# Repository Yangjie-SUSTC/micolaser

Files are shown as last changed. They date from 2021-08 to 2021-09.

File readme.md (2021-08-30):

# micolaser-1400

This is the a laserbox design used for microscope. 

There are four lasers: 405, 488,561,640. Excepet 488nm from toptica, all others made by new production laser, China.

Each laser reflected by 0.5 inch mirror and then to 1i inch dichroic mirror to combined into one beam, finally coipled into a single mode fiber by a fiber coupler from thorlabs.

In this depository, you can get all 3D and 2D drawings and part list fort it

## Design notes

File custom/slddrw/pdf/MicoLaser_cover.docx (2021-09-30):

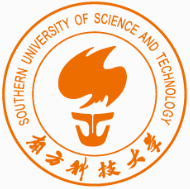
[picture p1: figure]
学校标识- 南方科技大学
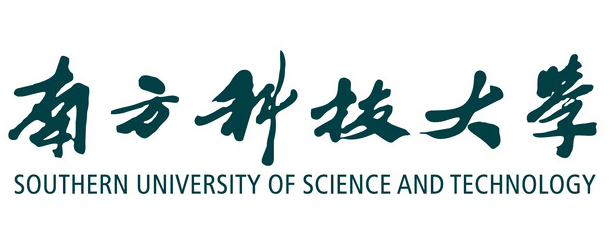
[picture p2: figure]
南方科技大学

MicoLaser-1400 图纸集

杨杰

yangj3@mail.sustech.edu.cn

https://github.com/Yangjie-SUSTC/micolaser

2021/9/30

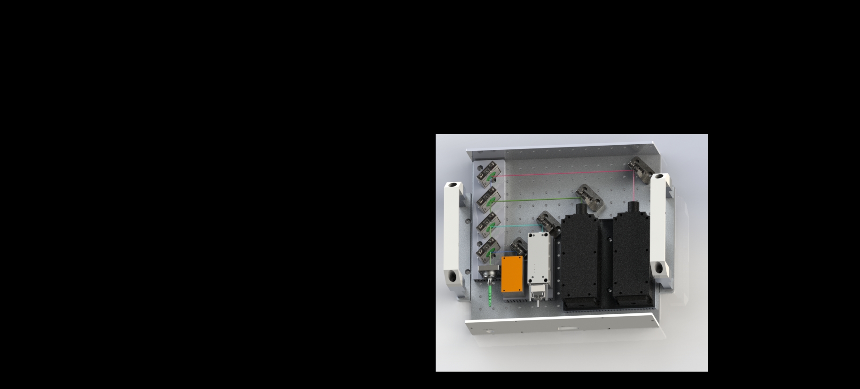
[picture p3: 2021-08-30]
内部渲染.JPG

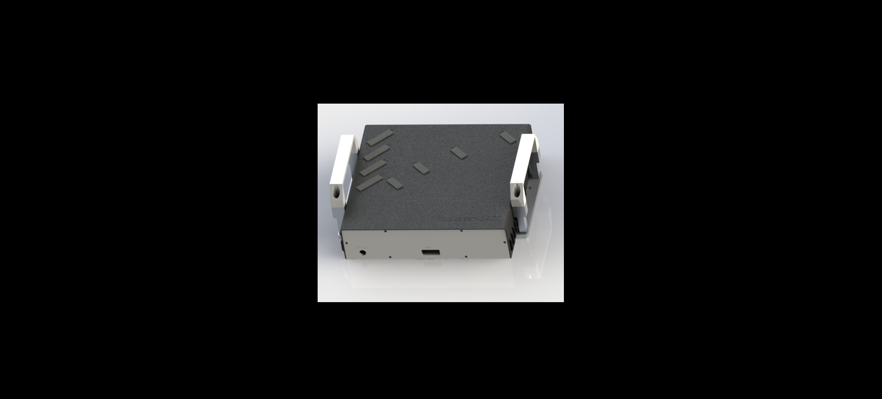
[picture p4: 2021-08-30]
外壳渲染.JPG

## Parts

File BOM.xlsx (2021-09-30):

No. | type | parts | catalog | paramater | manufacture | amount | price | total | link
1 | laser | 405nm | MDL-XS-405 | 200mw | xinchanye | 1 | 14500 | 14500 | http://www.cnilaser.com/PDF/MDL-XS-405.pdf
2 |  | 488nm | Toptica_ibeam_smart | 200mw | Toptica | 1 | 74000 | 74000
3 |  | 561nm | MGL-FN-561 | 300mw | xinchanye | 1 | 37500 | 37500 | http://www.cnilaser.com/PDF/MGL-FN-561.pdf
4 |  | 640nm | MRL-FN-639 | 300mw | xinchanye | 1 | 27000 | 27000 | http://www.cnilaser.com/PDF/MRL-FN-639.pdf
5 | mirror | 1 inch | PF10-03-P01 |  | thorlabs | 1 | 467.29 | 467.29 | PF10-03-P01 平面反射镜，有保护层的银膜，Ø1英寸 (thorlabs.com) (https://www.thorlabs.com/thorproduct.cfm?partnumber=PF10-03-P01)
6 |  | 0.5 inch | PF05-03-P01 |  | thorlabs | 4 | 286.41 | 1145.64 | PF05-03-P01 平面反射镜，有保护层的银膜，Ø1/2英寸 (thorlabs.com) (https://www.thorlabs.com/thorproduct.cfm?partnumber=PF05-03-P01)
7 | dichroic mirror |  | DMLP425 |  | thorlabs | 1 | 1594.96 | 1594.96 | DMLP425 长波通二向色镜，Ø1英寸，起始波长425 nm (thorlabs.com) (https://www.thorlabs.com/thorproduct.cfm?partnumber=DMLP425)
8 |  |  | DMLP505 |  | thorlabs | 1 | 1594.96 | 1594.96 | https://www.thorlabs.com/thorproduct.cfm?partnumber=DMLP505
9 |  |  | DMLP605 |  | thorlabs | 1 | 1594.96 | 1594.96 | https://www.thorlabs.com/thorproduct.cfm?partnumber=DMLP605
10 | fiber output | single mode fiber | P3-405BPM-FC-2 |  | thorlabs | 1 | 1000 | 1000 | https://www.thorlabs.com/thorproduct.cfm?partnumber=P3-405BPM-FC-2
11 |  | fiber coupler | PAF2-A4A |  | thorlabs | 1 | 5460 | 5460 | https://www.thorlabs.com/thorproduct.cfm?partnumber=PAF2-A4A
12 | adjuster |  | hvm-s1r |  | Newport | 1 | 1500 | 1500 | HVM-S1r 反射镜调整架，工业，垂直驱动，1 英寸，2个锁定内六角扳手 (newport.com.cn) (https://www.newport.com.cn/p/HVM-S1r)
13 |  |  | hvm-s1t |  | Newport | 3 | 1600 | 4800 | HVM-S1t 反射镜调整架，工业，垂直驱动，1 英寸，2个锁定内六角扳手 (newport.com.cn) (https://www.newport.com.cn/p/HVM-S1t)
14 |  |  | HVM-05r |  | Newport | 4 | 1360 | 5440 | HVM-05r 反射镜调整架，工业，垂直驱动，后部装载，0.5 英寸， 2个锁定内六角扳手 (newport.com.cn) (https://www.newport.com.cn/p/HVM-05r)
15 |  | Handle | 180mm |  | taobao | 2 | 15 | 30 | 加厚铝合金黑色明装拉手/柜门把手/明装工业设备拉手/工具箱提手-淘宝网 (taobao.com) (https://item.taobao.com/item.htm?id=582286161723&ali_trackid=1_329b5c05201caaaba83558623b89cd20)
16 | magnatic bar | long | 18*60*3 |  | taobao | 4 | 3 | 12 | 宽18*厚2mm K橡胶磁铁条贴 强力软磁条 橡胶磁铁软磁条-淘宝网 (taobao.com) (https://item.taobao.com/item.htm?spm=a230r.1.14.36.3ce538a7w06UFg&id=652351358299&ns=1&abbucket=8)
17 |  | short | 18*40*3 |  | taobao | 4 | 3 | 12
18 | heatsink | 561-640 | 1_561-640nm_heatsink | 6061 Al | custom | 1 | 700 | 700
19 |  |  | 2_405-488nm_heatsink | 6062 Al | custom | 1 | 800 | 800
20 | base |  | 3_DM_base | stainless steel | custom | 1 | 1000 | 1000
21 |  |  | 4_fiberport_stage | stainless steel | custom | 1 | 300 | 300
22 |  |  | 5_0.5mir_base | stainless steel | custom | 1 | 500 | 500
23 |  |  | 6_base | stainless steel | custom | 1 | 2000 | 2000
24 | cover |  | 7_shell | steel | custom | 1 | 2000 | 2000
25 |  |  | 8_back_panel | PMMA | custom | 1 | 200 | 200
26 |  |  | 9_front_panel | PMMA | custom | 1 | 200 | 200
27 |  |  | 10_handle_base | Al | custom | 4 | 100 | 400
28 | pin |  | Φ4*8mm | HPA-2X8-SUS | Misumi | 16 | 6.84 | 109.44 | 圆柱销 A型 m6正公差_价格_多少钱_图片-米思米官网 (misumi.com.cn) (https://www.misumi.com.cn/vona2/detail/221000596791/?pageName=PageCategory)
29 |  |  | Φ2.4*5mm |  |  | 8 | 0.1 | 0.8 | https://item.taobao.com/item.htm?id=530385435625&ns=1&abbucket=15 (https://item.taobao.com/item.htm?spm=a230r.1.14.1.5ab23954NWDenb&id=530385435625&ns=1&abbucket=15)
30 |  |  | Φ1.6*5mm | HPA-1.6X8-SUS |  | 4 | 5.4 | 21.6 | 定位销 圆柱型/A型/m6正公差_价格_多少钱_图片-米思米官网 (misumi.com.cn) (https://www.misumi.com.cn/vona2/detail/221000596791/?pageName=PageCategory)
31 | screw |  | M6*12mm |  | taobao | 17 | 1 | 17
32 |  |  | M4*8mm |  | taobao | 28 | 1 | 28
33 |  |  | M3*6mm |  | taobao | 16 | 0.5 | 8
34 |  |  |  |  |  |  | total | 185936.65

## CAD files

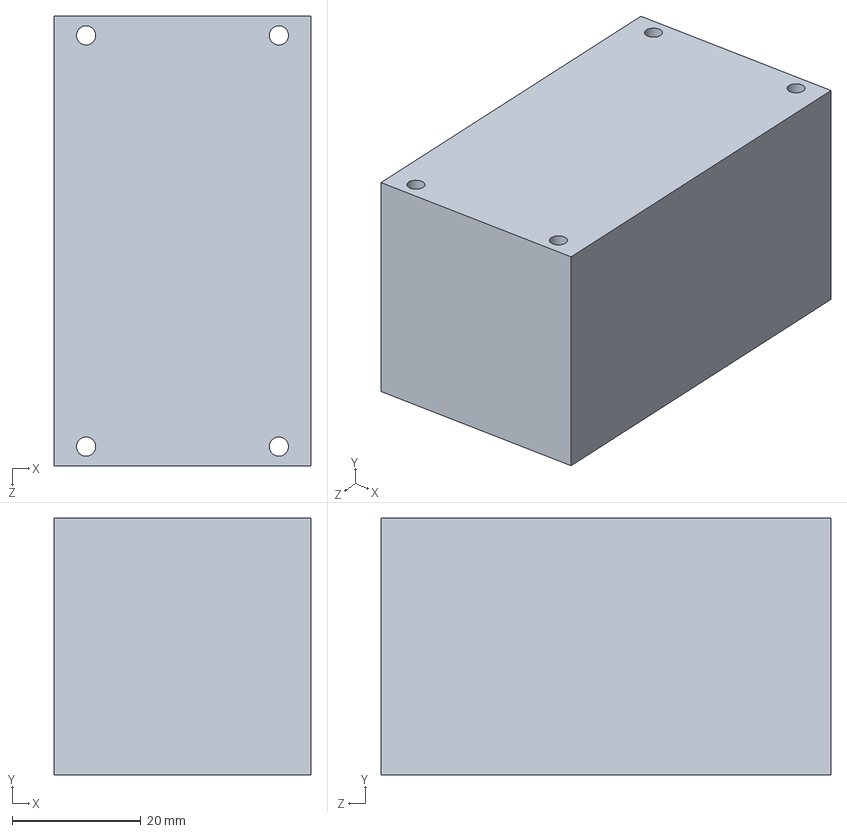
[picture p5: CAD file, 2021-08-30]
commecial/laser/MDL-XS-405.SLDPRT
40.0 x 40.0 x 70.0 mm

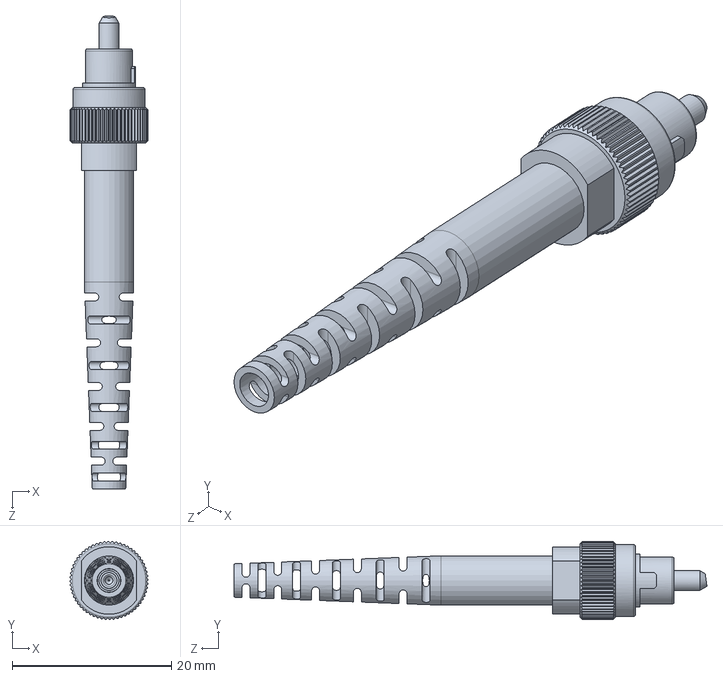
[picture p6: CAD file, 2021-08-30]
commecial/optics/P3-405BPM-FC-2-fiber.sldprt
9.84 x 9.84 x 59.4 mm

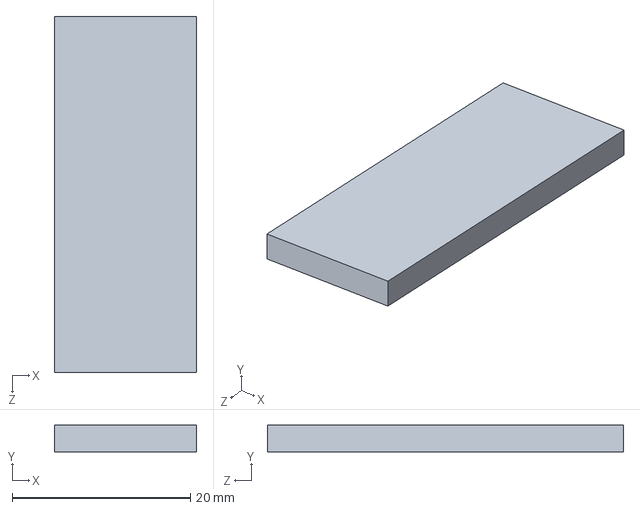
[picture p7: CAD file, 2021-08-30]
commecial/短磁条.SLDPRT
16.0 x 3.00 x 40.0 mm

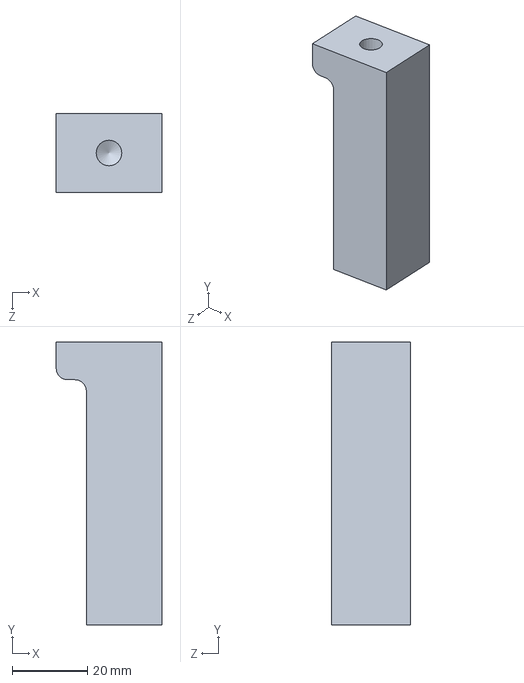
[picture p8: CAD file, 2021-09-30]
custom/10_handle_base.SLDPRT
28.0 x 75.0 x 21.0 mm

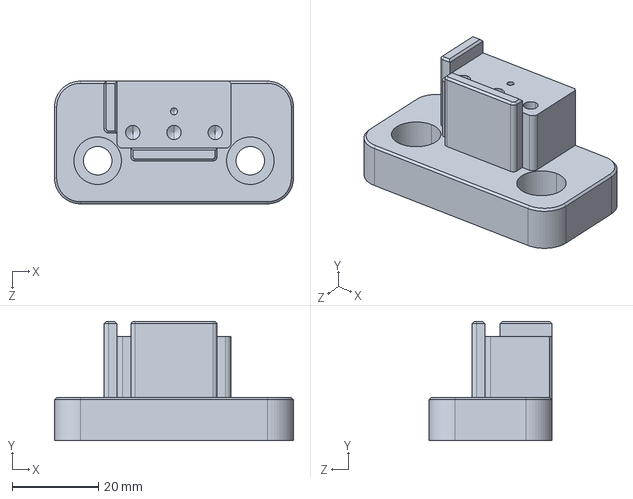
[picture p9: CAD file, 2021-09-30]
custom/micolase1400加工图纸集20210930_南科大/step/5_0.5mir_base.STEP
55.4 x 27.6 x 28.4 mm

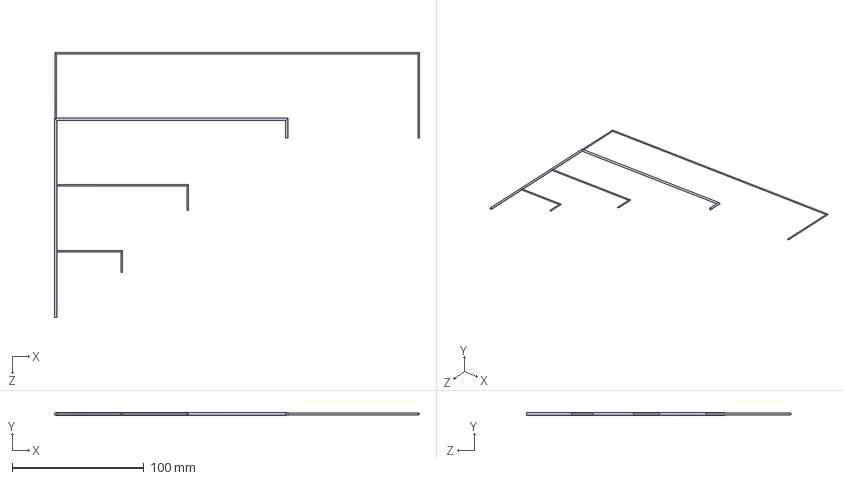
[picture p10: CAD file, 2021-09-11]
optical_path.SLDPRT
276.6 x 2.00 x 200.6 mm

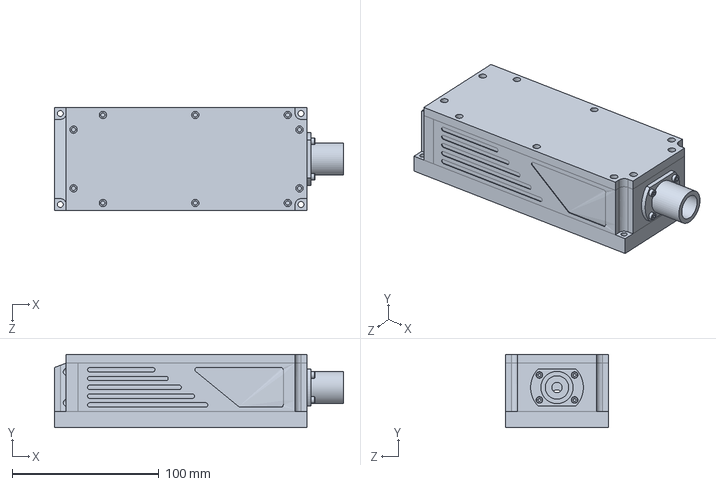
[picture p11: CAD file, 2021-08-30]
commecial/laser/MRL-FN-639.SLDPRT
197.0 x 50.0 x 70.0 mm

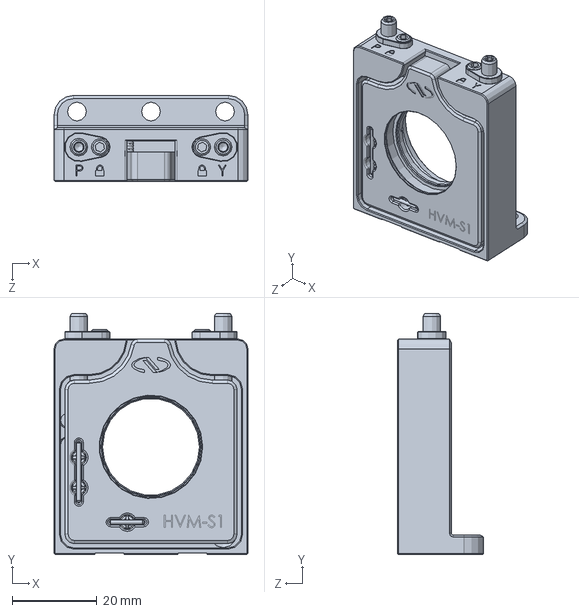
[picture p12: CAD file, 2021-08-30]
commecial/optics/hvm-s1t.SLDPRT
45.7 x 56.8 x 20.3 mm

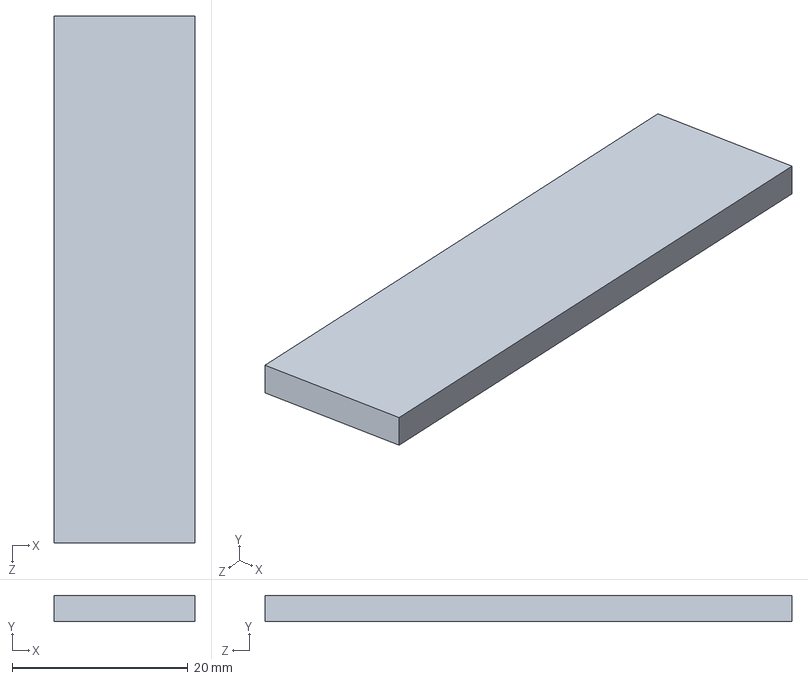
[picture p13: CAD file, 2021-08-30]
commecial/长磁条.SLDPRT
16.0 x 3.00 x 60.0 mm

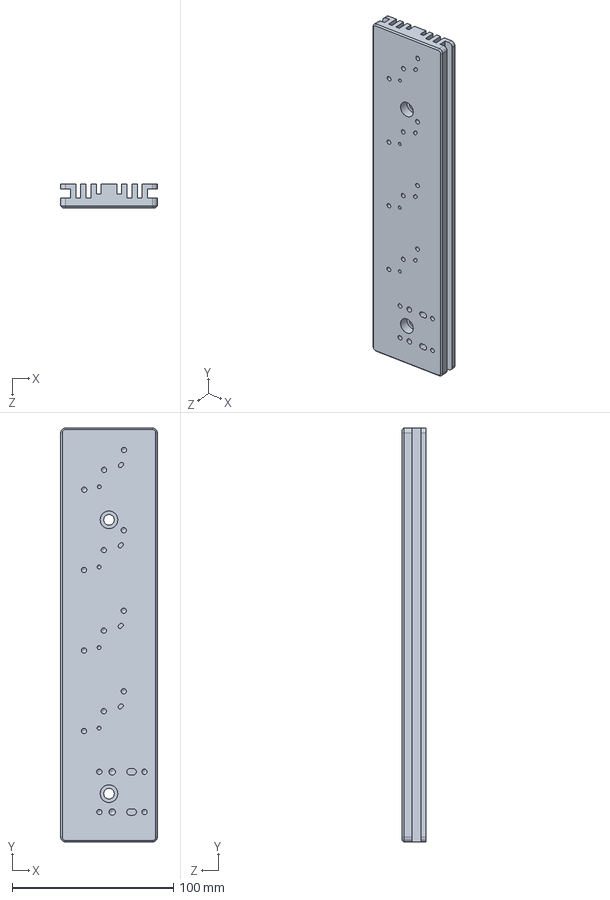
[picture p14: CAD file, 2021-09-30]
custom/3_DM_base.SLDPRT
60.0 x 257.0 x 14.6 mm

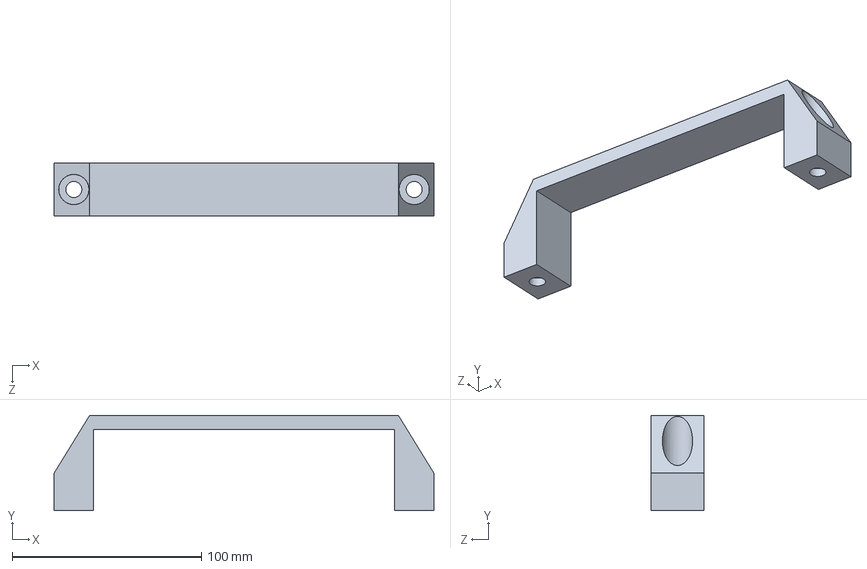
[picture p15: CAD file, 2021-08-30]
commecial/0_Handle.SLDPRT
201.0 x 50.5 x 28.0 mm

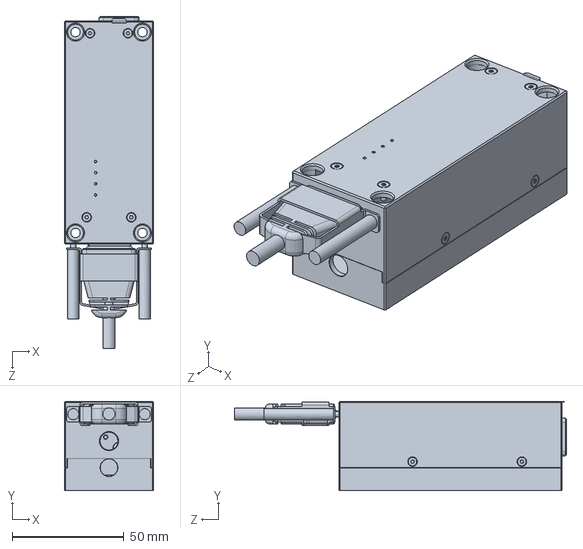
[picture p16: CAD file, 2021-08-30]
commecial/laser/Toptica_ibeam_smart.SLDPRT
40.0 x 40.0 x 148.8 mm

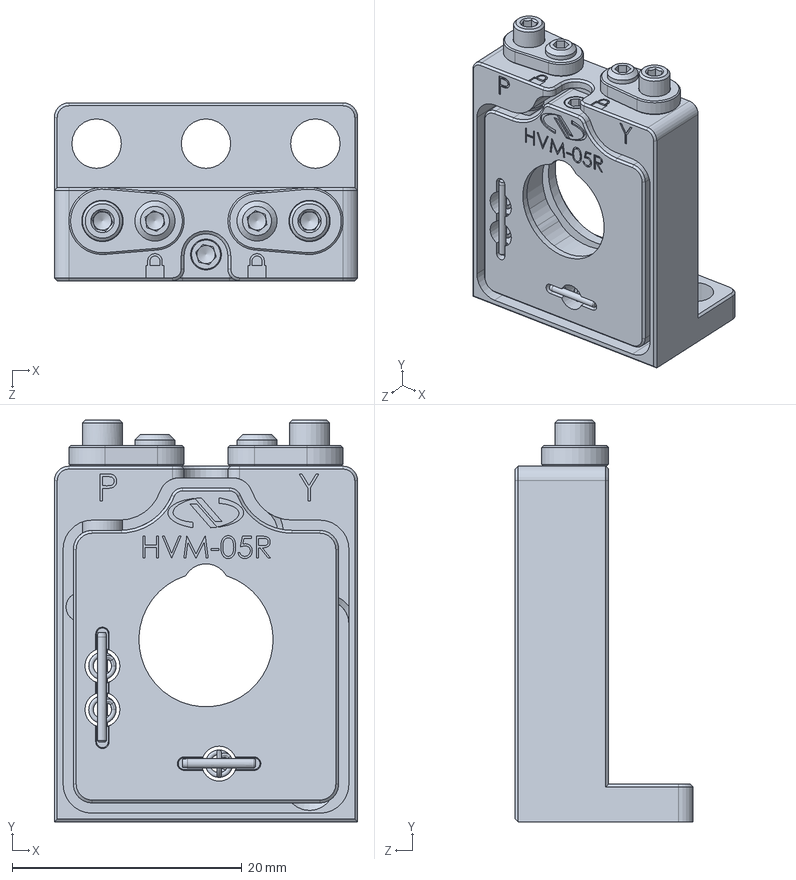
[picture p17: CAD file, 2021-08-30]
commecial/optics/HVM-05r.SLDPRT
26.4 x 35.0 x 15.5 mm

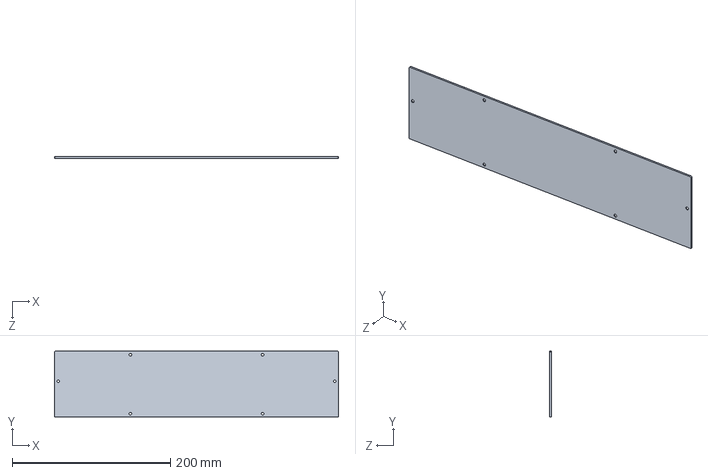
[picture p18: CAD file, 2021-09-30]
custom/8_back_panel.SLDPRT
359.0 x 83.0 x 2.00 mm

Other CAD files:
custom/micolase1400加工图纸集20210930_南科大/dwg/总装.DWG
custom/slddrw/dwg/2_405-488nm_heatsink.DWG
custom/micolase1400加工图纸集20210930_南科大/step/3_DM_base.STEP
custom/slddrw/dwg/1_561-640nm_heatsink.DWG
commecial/optics/hvm-s1r.SLDPRT
commecial/optics/mirror/1inch_Mirror_thorlabs_PF10-03-P01_450nm.SLDPRT
commecial/optics/mirror/DMLP425_thorlabs.sldprt
commecial/optics/mirror/PF05-03-P01-10-thorlabs.sldprt
custom/1_561-640nm_heatsink.SLDPRT
custom/2_405-488nm_heatsink.SLDPRT
custom/4_fiberport_stage.SLDPRT
custom/5_0.5mir_base.SLDPRT
custom/6_base.SLDPRT
custom/7_shell.SLDPRT
custom/9_front_panel.SLDPRT
custom/micolase1400加工图纸集20210930_南科大/dwg/10_handle_base.DWG
custom/micolase1400加工图纸集20210930_南科大/dwg/1_561-640nm_heatsink.DWG
custom/micolase1400加工图纸集20210930_南科大/dwg/2_405-488nm_heatsink.DWG
custom/micolase1400加工图纸集20210930_南科大/dwg/3_DM_base.DWG
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

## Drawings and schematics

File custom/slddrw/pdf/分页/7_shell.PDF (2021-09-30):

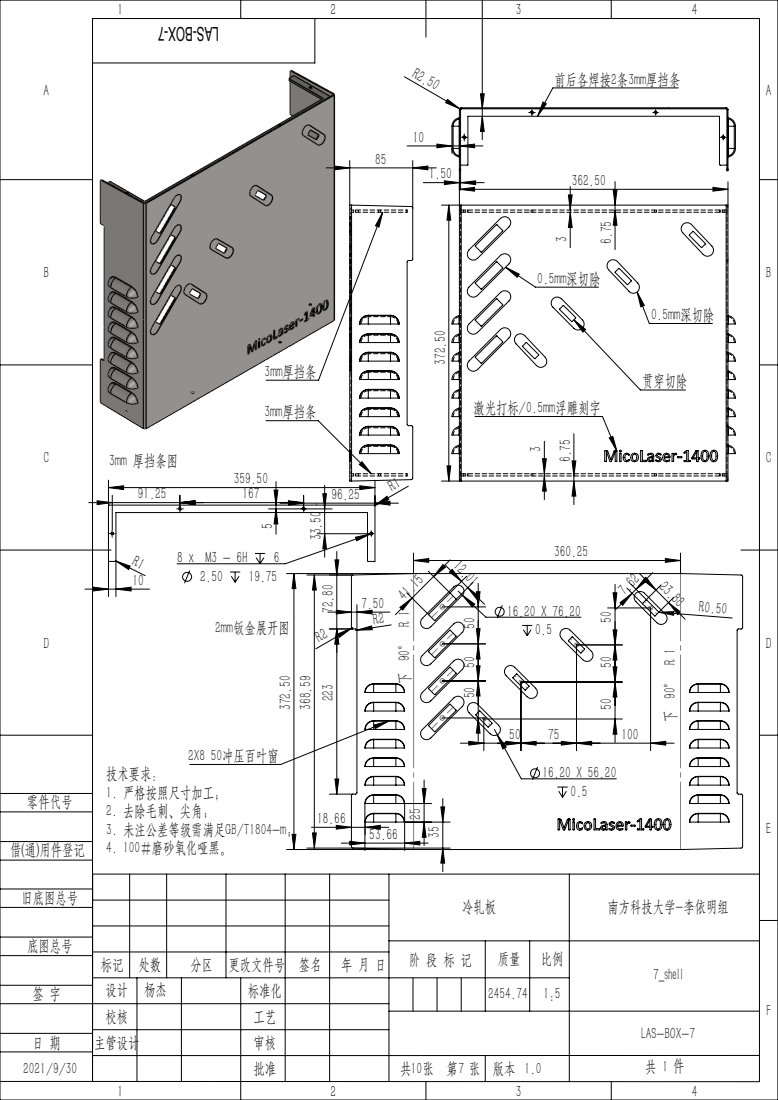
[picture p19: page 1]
2X8 50冲压百叶窗; 3mm 厚挡条图; 1. 严格按照尺寸加工； 2. 去除毛刺、尖角； 3. 未注公差等级需满足GB/T1804-m； 4. 100#磨砂氧化哑黑。

冷轧板 | 南方科技大学-李依明组

阶 段 标 记 | 质量 | 比例 | 7_shell

标记 | 处数 | 分区 | 更改文件号 | 签名 | 年 月 日
设计 | 杨杰 | | 标准化 | | | | | | 2454.74 | 1:5
校核 | | | 工艺
主管设计 | | | 审核

LAS-BOX-7

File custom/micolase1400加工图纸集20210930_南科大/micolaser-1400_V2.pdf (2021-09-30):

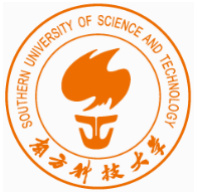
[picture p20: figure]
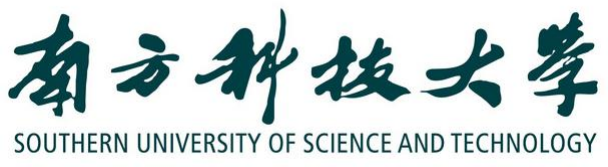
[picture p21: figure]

# MicoLaser-1400 图纸集

杨杰

## yangj3@mail.sustech.edu.cn

## https://github.com/Yangjie-SUSTC/micolaser

2021/9/30

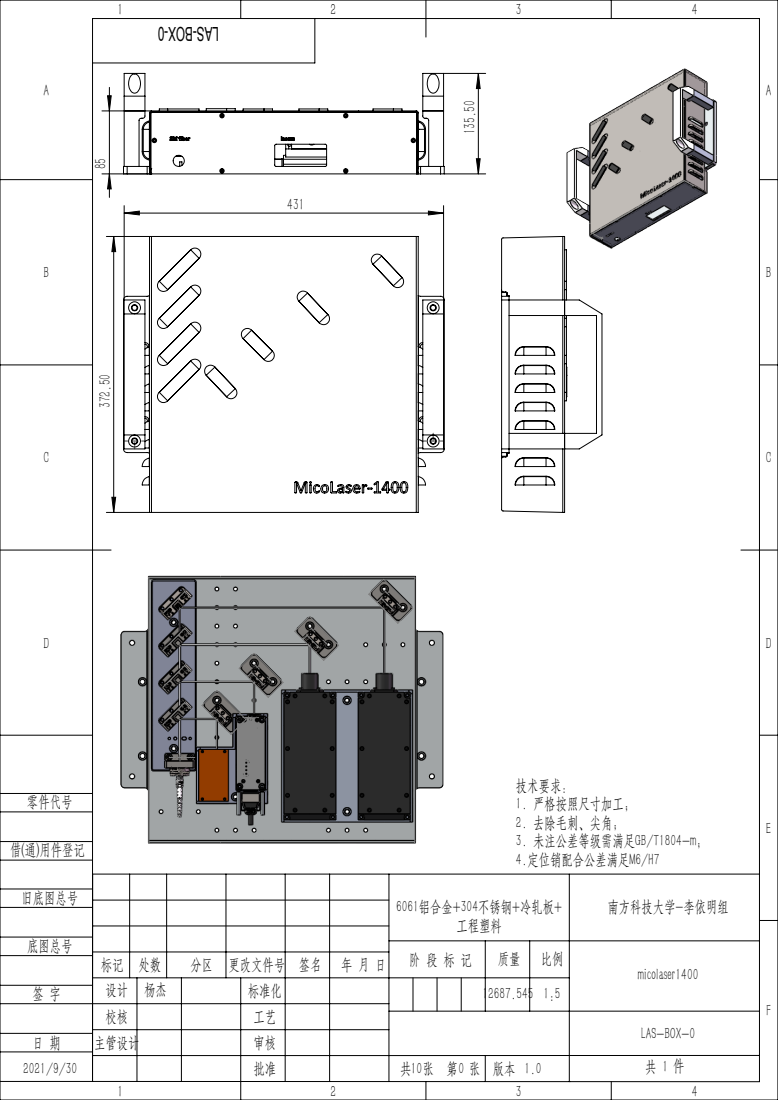
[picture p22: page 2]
底图总号; 旧底图总号; 借(通)用件登记; 零件代号; 技术要求： 1. 严格按照尺寸加工； 2. 去除毛刺、尖角； 3. 未注公差等级需满足GB/T1804-m； 4.定位销配合公差满足M6/H7

6061铝合金+304不锈钢+冷轧板+ 工程塑料 | 南方科技大学-李依明组

阶 段 标 记 | 质量 | 比例 | micolaser1400

标记 | 处数 | 分区 | 更改文件号 | 签名 | 年 月 日
设计 | 杨杰 | | 标准化 | | | | | | 12687.545 | 1:5
校核 | | | 工艺
主管设计 | | | 审核

LAS-BOX-0

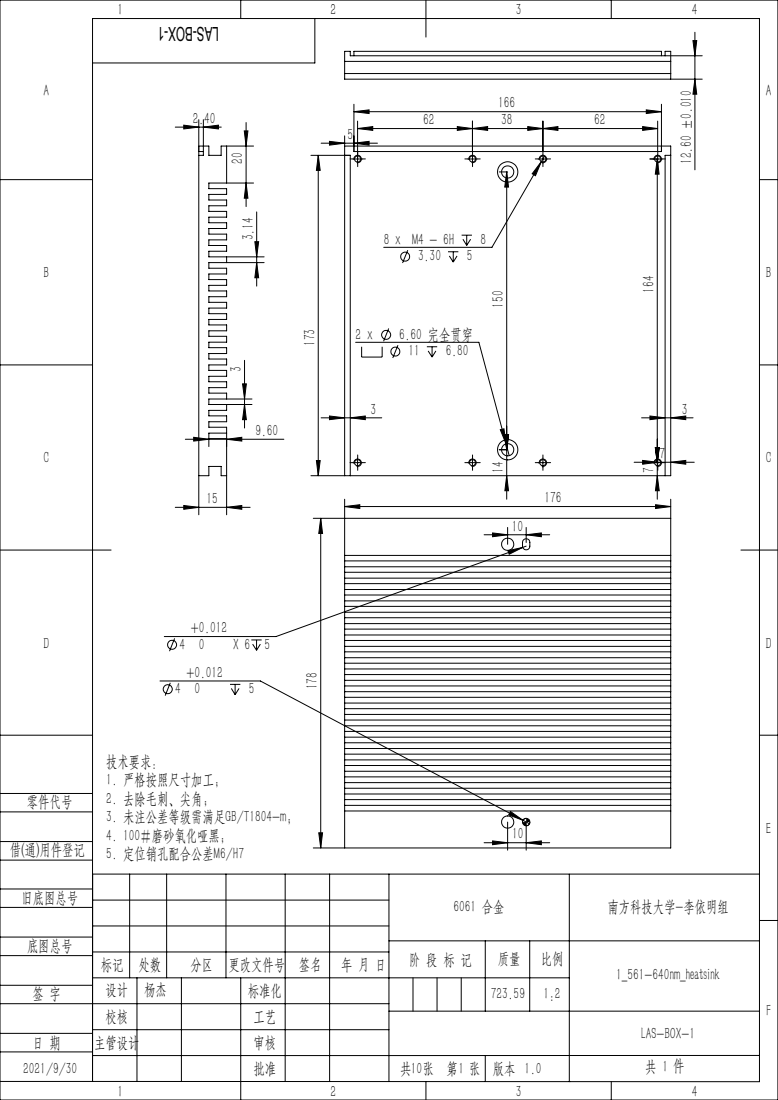
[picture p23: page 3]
6.60 完全贯穿; 底图总号; 旧底图总号; 借(通)用件登记; 零件代号; 技术要求： 1. 严格按照尺寸加工； 2. 去除毛刺、尖角； 3. 未注公差等级需满足GB/T1804-m； 4. 100#磨砂氧化哑黑; 5. 定位销孔配合公差M6/H7

6061 合金 | 南方科技大学-李依明组

阶 段 标 记 | 质量 | 比例 | 1_561-640nm_heatsink

标记 | 处数 | 分区 | 更改文件号 | 签名 | 年 月 日
设计 | 杨杰 | | 标准化 | | | 723.59 | 1:2

24.13 ¹³

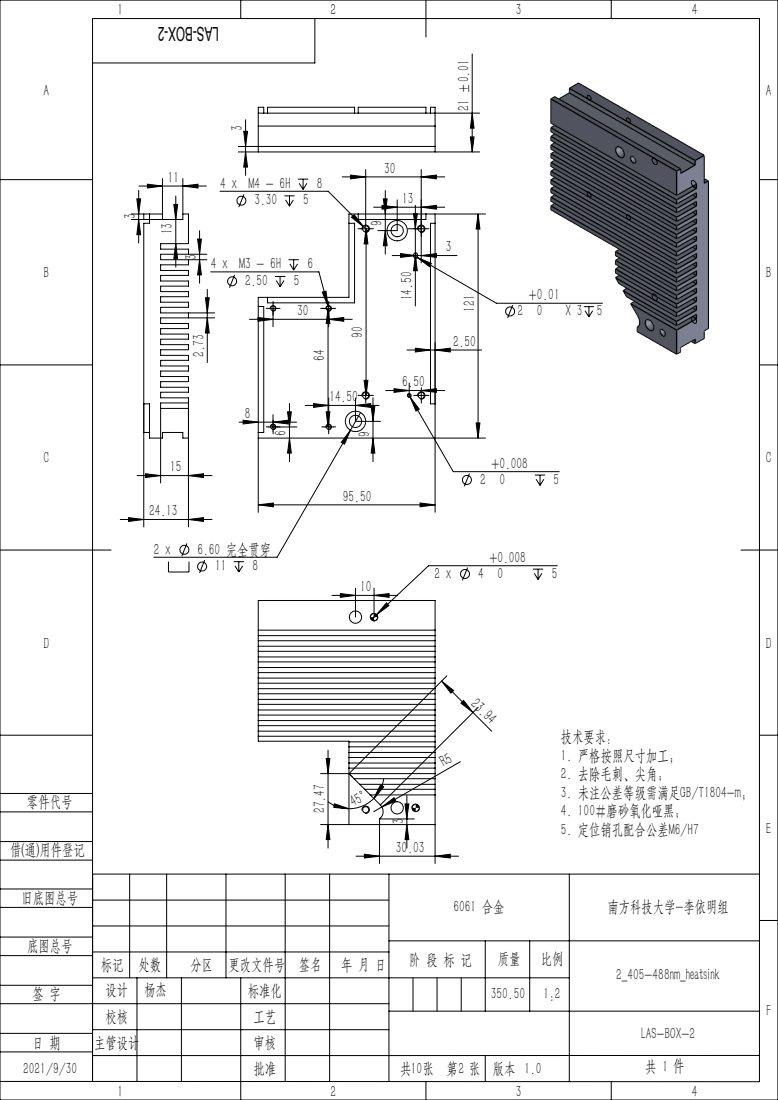
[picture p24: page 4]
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

6061 合金 | 南方科技大学-李依明组

阶 段 标 记 | 质量 | 比例 | 2_405-488nm_heatsink

标记 | 处数 | 分区 | 更改文件号 | 签名 | 年 月 日
设计 | 杨杰 | | 标准化 | | | 350.50 | 1:2

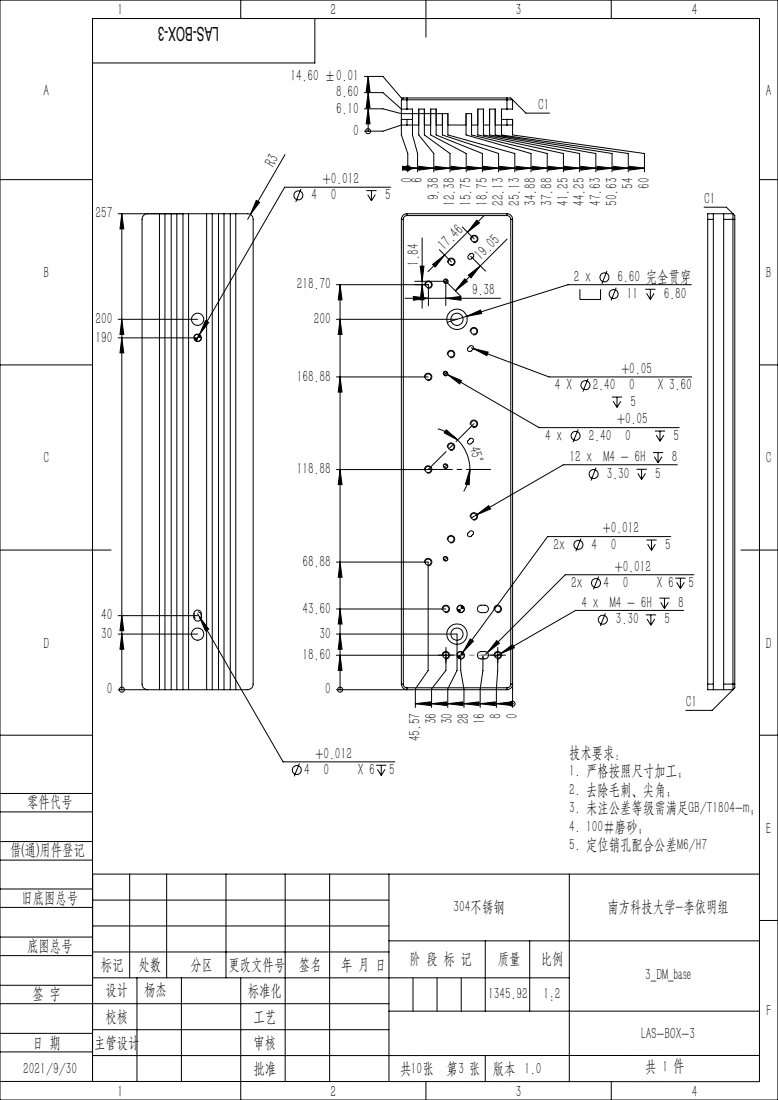
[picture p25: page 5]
6.60 完全贯穿; 底图总号; 旧底图总号; 借(通)用件登记; 零件代号; 技术要求： 1. 严格按照尺寸加工； 2. 去除毛刺、尖角； 3. 未注公差等级需满足GB/T1804-m； 4. 100#磨砂; 5. 定位销孔配合公差M6/H7

304不锈钢 | 南方科技大学-李依明组

阶 段 标 记 | 质量 | 比例 | 3_DM_base

标记 | 处数 | 分区 | 更改文件号 | 签名 | 年 月 日
设计 | 杨杰 | | 标准化 | | | 1345.92 | 1:2

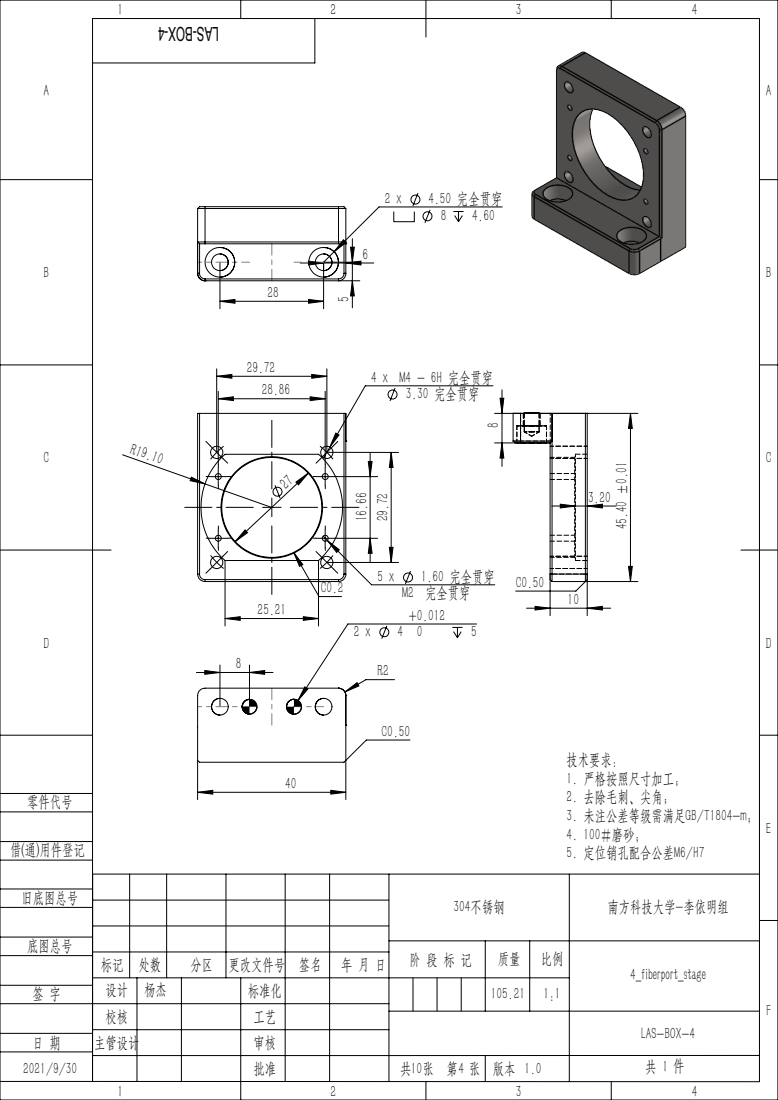
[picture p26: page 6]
4 x M4 - 6H 完全贯穿 3.30 完全贯穿; 1.60 完全贯穿 C0.2; M2 完全贯穿; 4.50 完全贯穿; 底图总号; 旧底图总号; 借(通)用件登记; 零件代号; 技术要求： 1. 严格按照尺寸加工； 2. 去除毛刺、尖角； 3. 未注公差等级需满足GB/T1804-m； 4. 100#磨砂； 5. 定位销孔配合公差M6/H7

304不锈钢 | 南方科技大学-李依明组

阶 段 标 记 | 质量 | 比例 | 4_fiberport_stage

标记 | 处数 | 分区 | 更改文件号 | 签名 | 年 月 日
设计 | 杨杰 | | 标准化 | | | 105.21 | 1:1

11 6.80 ¹⁰

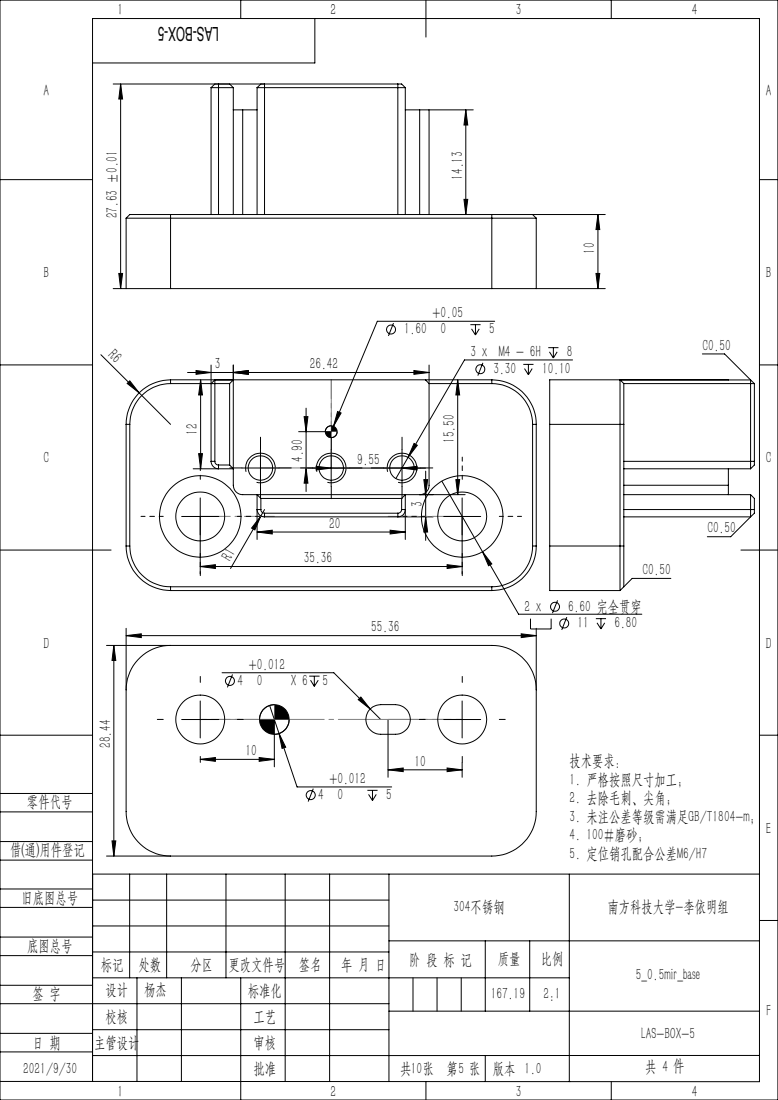
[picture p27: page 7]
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

304不锈钢 | 南方科技大学-李依明组

阶 段 标 记 | 质量 | 比例 | 5_0.5mir_base

标记 | 处数 | 分区 | 更改文件号 | 签名 | 年 月 日
设计 | 杨杰 | | 标准化 | | | 167.19 | 2:1

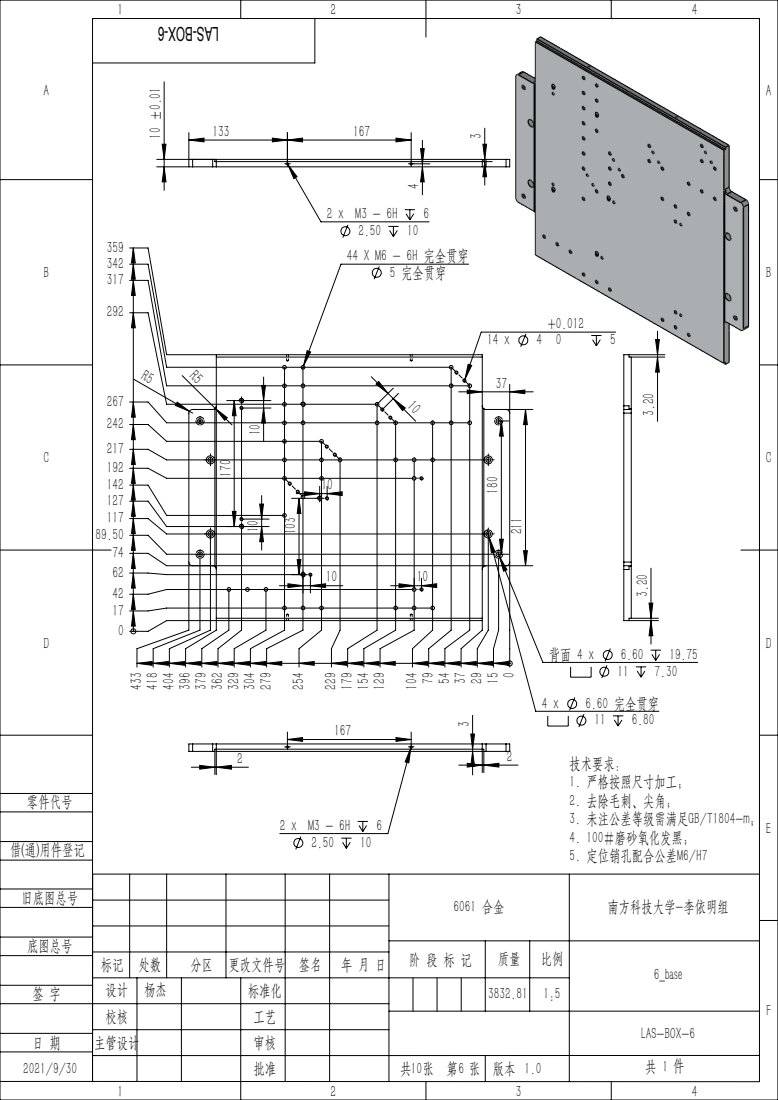
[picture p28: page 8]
44 X M6 - 6H 完全贯穿 5 完全贯穿; 6.60 完全贯穿; 底图总号; 旧底图总号; 借(通)用件登记; 零件代号; 技术要求： 1. 严格按照尺寸加工； 2. 去除毛刺、尖角； 3. 未注公差等级需满足GB/T1804-m； 4. 100#磨砂氧化发黑; 5. 定位销孔配合公差M6/H7

6061 合金 | 南方科技大学-李依明组

阶 段 标 记 | 质量 | 比例 | 6_base

标记 | 处数 | 分区 | 更改文件号 | 签名 | 年 月 日
设计 | 杨杰 | | 标准化 | | | 3832.81 | 1:5

激光打标/0.5mm浮雕刻字; 0.5mm深切除; 贯穿切除; 3mm厚挡条; 前后各焊接2条3mm厚挡条; 2X8 50冲压百叶窗; 2mm钣金展开图; 3mm 厚挡条图; 底图总号; 旧底图总号; 借(通)用件登记; 零件代号; 技术要求： 1. 严格按照尺寸加工； 2. 去除毛刺、尖角； 3. 未注公差等级需满足GB/T1804-m； 4. 100#磨砂氧化哑黑。

冷轧板 | 南方科技大学-李依明组

阶 段 标 记 | 质量 | 比例 | 7_shell

标记 | 处数 | 分区 | 更改文件号 | 签名 | 年 月 日
设计 | 杨杰 | | 标准化 | | | 2454.74 | 1:5

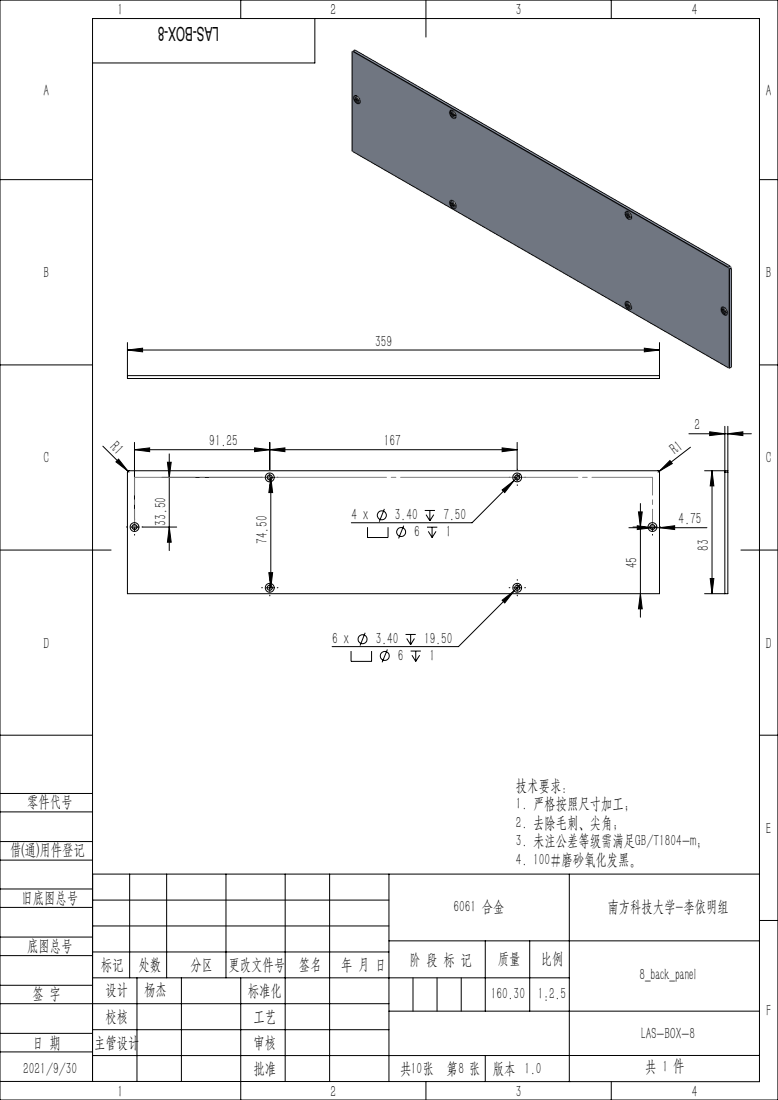
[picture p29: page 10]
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

6061 合金 | 南方科技大学-李依明组

阶 段 标 记 | 质量 | 比例 | 8_back_panel

标记 | 处数 | 分区 | 更改文件号 | 签名 | 年 月 日
设计 | 杨杰 | | 标准化 | | | 160.30 | 1:2.5

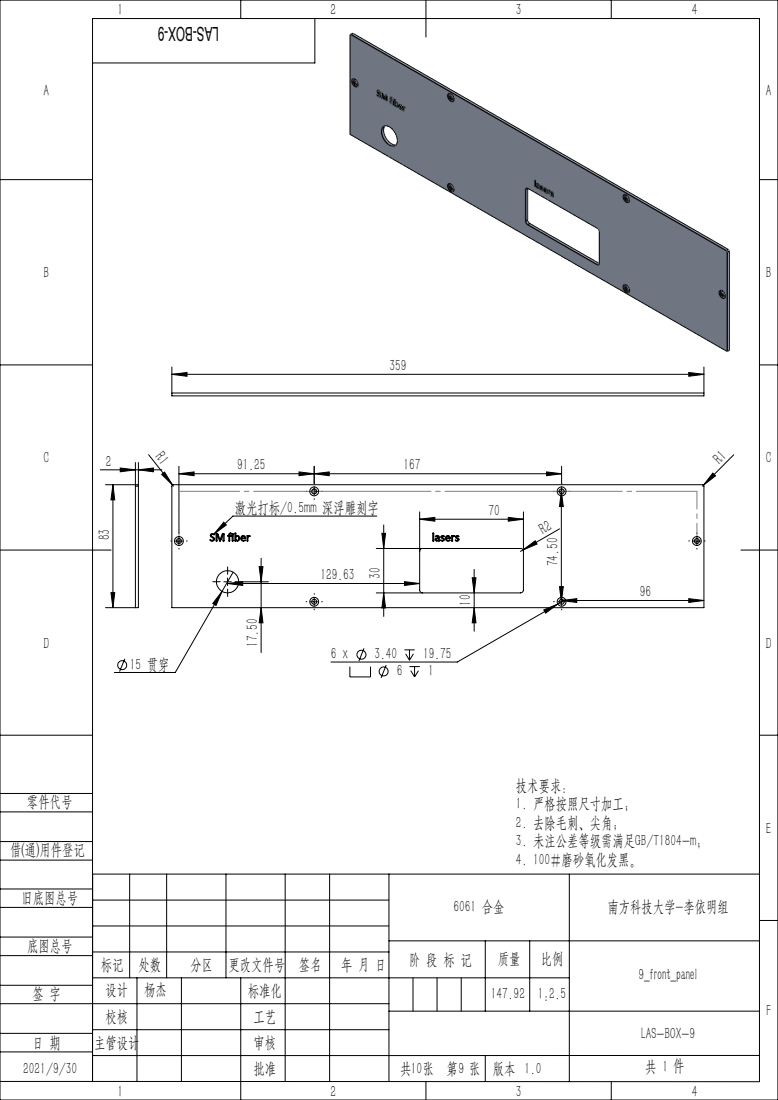
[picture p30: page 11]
激光打标/0.5mm 深浮雕刻字; 底图总号; 旧底图总号; 借(通)用件登记; 零件代号; 技术要求： 1. 严格按照尺寸加工； 2. 去除毛刺、尖角； 3. 未注公差等级需满足GB/T1804-m； 4. 100#磨砂氧化发黑。

6061 合金 | 南方科技大学-李依明组

阶 段 标 记 | 质量 | 比例 | 9_front_panel

标记 | 处数 | 分区 | 更改文件号 | 签名 | 年 月 日
设计 | 杨杰 | | 标准化 | | | 147.92 | 1:2.5

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

6061 合金 | 南方科技大学-李依明组

阶 段 标 记 | 质量 | 比例 | 10_handle_base

标记 | 处数 | 分区 | 更改文件号 | 签名 | 年 月 日
设计 | 杨杰 | | 标准化 | | | 86.51 | 1:1

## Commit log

2021-09-11 v2 change heatsink,reduce shell to 1.5mm, dm base, remove base hole without out 2d draw
    [10_handle_base.STEP, 1_561-640nm_heatsink.SLDPRT, 1_561-640nm_heatsink.STEP, 2_405-488nm_heatsink.SLDPRT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]
2021-09-30 mifigy shell ans base for manufaction
    [10_handle_base.DWG, 10_handle_base.SLDDRW, 10_handle_base.SLDPRT, 10_handle_base.STEP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]
2021-09-30 send to factory 20210930
    [BOM.xlsx]
